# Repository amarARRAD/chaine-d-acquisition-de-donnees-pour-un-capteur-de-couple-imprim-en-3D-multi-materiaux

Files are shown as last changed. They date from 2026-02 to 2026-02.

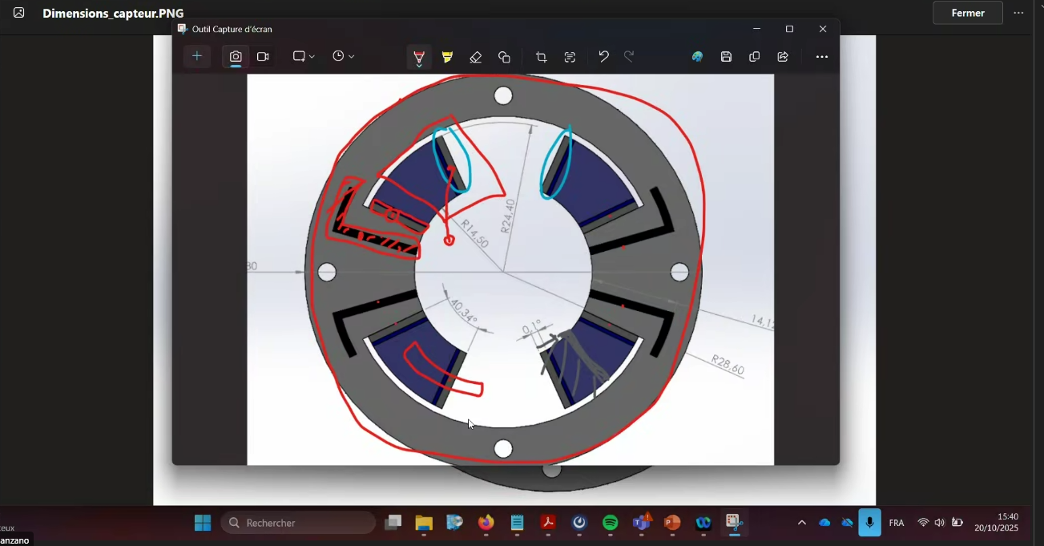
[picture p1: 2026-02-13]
Biblio/Biblio/Capture d'écran 2025-10-20 154038.png

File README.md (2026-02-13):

# Chaîne d’acquisition pour capteur de couple capacitif imprimé en 3D (ESP32-S3 + FDC1004)

Ce dépôt regroupe le travail réalisé dans le cadre du Master 2 EEEA (Systèmes embarqués) en collaboration avec l’Inria.  
Le projet vise à rendre autonome la mesure de couple d’un capteur capacitif imprimé en 3D multi-matériaux, destiné à une intégration dans un exosquelette.

## Principe
Le capteur comporte 4 structures capacitives. Lorsqu’un couple est appliqué, la déformation mécanique provoque des variations de capacité. Ces 4 mesures sont combinées pour obtenir une grandeur différentielle, puis un angle et enfin un couple estimé.

## Architecture matérielle
- **FDC1004** : convertisseur capacité-numérique (4 canaux) avec **blindage actif** (/Blinddd) pour limiter les capacités parasites.
- **ESP32-S3-WROOM-1** : récupération des mesures via **I2C**, traitement embarqué et communication.
- **PCB circulaire 2 couches** conçu pour être monté directement sur le capteur (plan de masse + plan de blindage).
- Interfaces prévues : **UART** (programmation / debug) et **CAN** (prévu pour intégration future exosquelette).

## Logiciel embarqué
Le traitement initialement réalisé sous MATLAB a été traduit en **C++ (ESP-IDF)** sous forme de librairie :
- driver I2C FDC1004 (lecture des 4 capacités, conversion en pF)
- calcul de la capacité différentielle (`Ctot`)
- estimation d’angle et de couple (modèle statique avec hystérésis + terme dynamique)

## Contenu du dépôt
- Fichiers **KiCad** (schéma + routage + fabrication)
- Code **C++ / ESP-IDF** (librairie capteur + exemples)
- Rapport (LaTeX) et annexes (datasheets / documents)

## Perspectives
- réintégration d’une **Flash externe**
- ajout de **filtrage numérique**
- ajout de capteurs complémentaires (température, IMU) pour améliorer la robustesse en conditions réelles

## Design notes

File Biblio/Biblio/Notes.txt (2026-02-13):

[1] Contexte du capteur : exosquelette développé à Rennes
[2] Caractérisation de la version actuelle du capteur de couple
[3] Capteur de couple similaire
[4] Algorithme de suivi d'hystérésis
[5] Mesure de capacités avec blindage (voir notamment section 6.2)

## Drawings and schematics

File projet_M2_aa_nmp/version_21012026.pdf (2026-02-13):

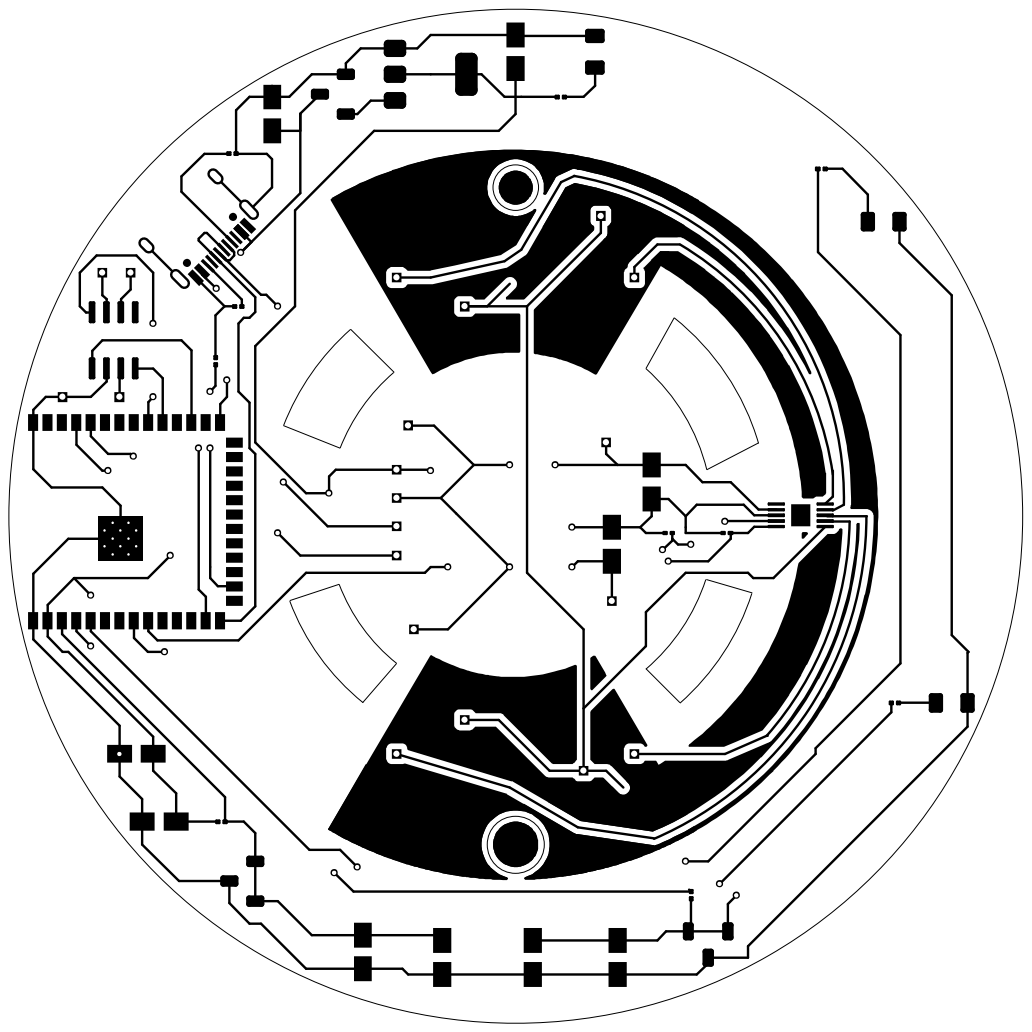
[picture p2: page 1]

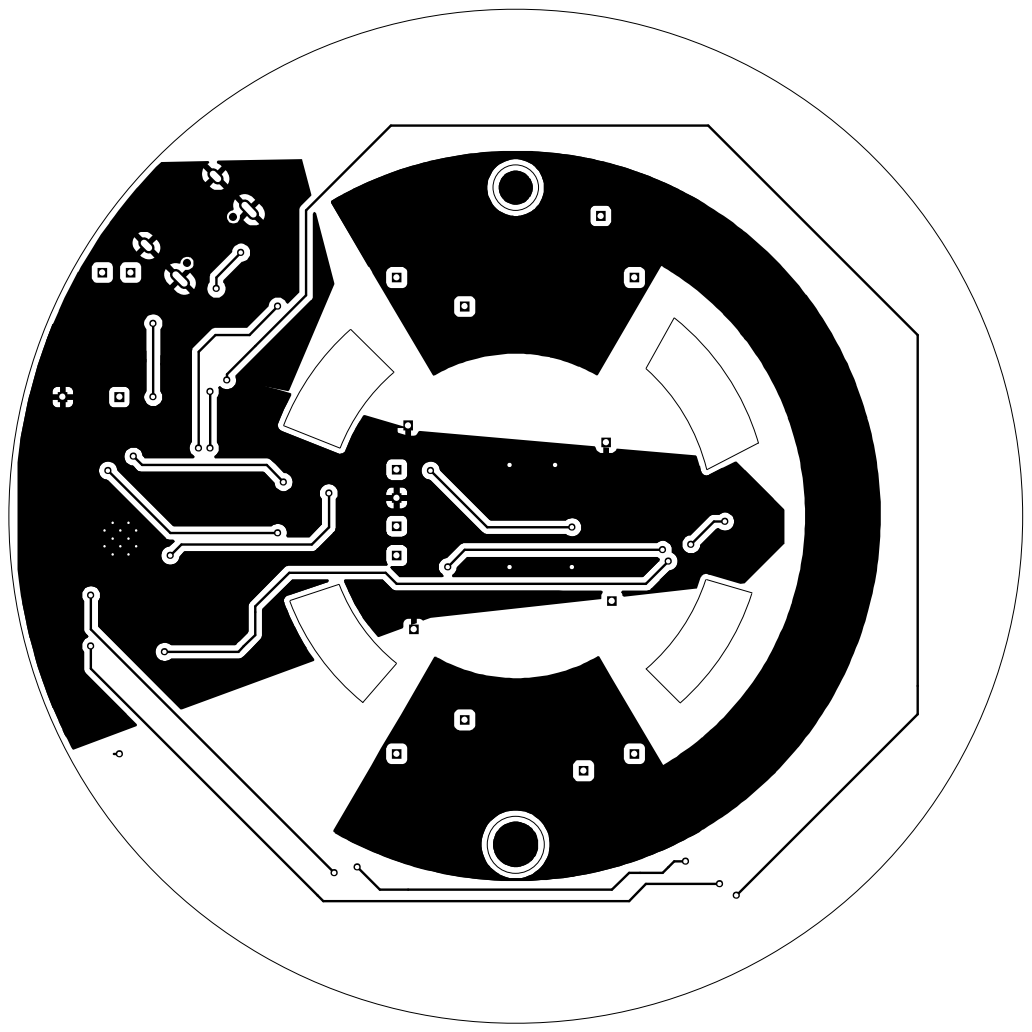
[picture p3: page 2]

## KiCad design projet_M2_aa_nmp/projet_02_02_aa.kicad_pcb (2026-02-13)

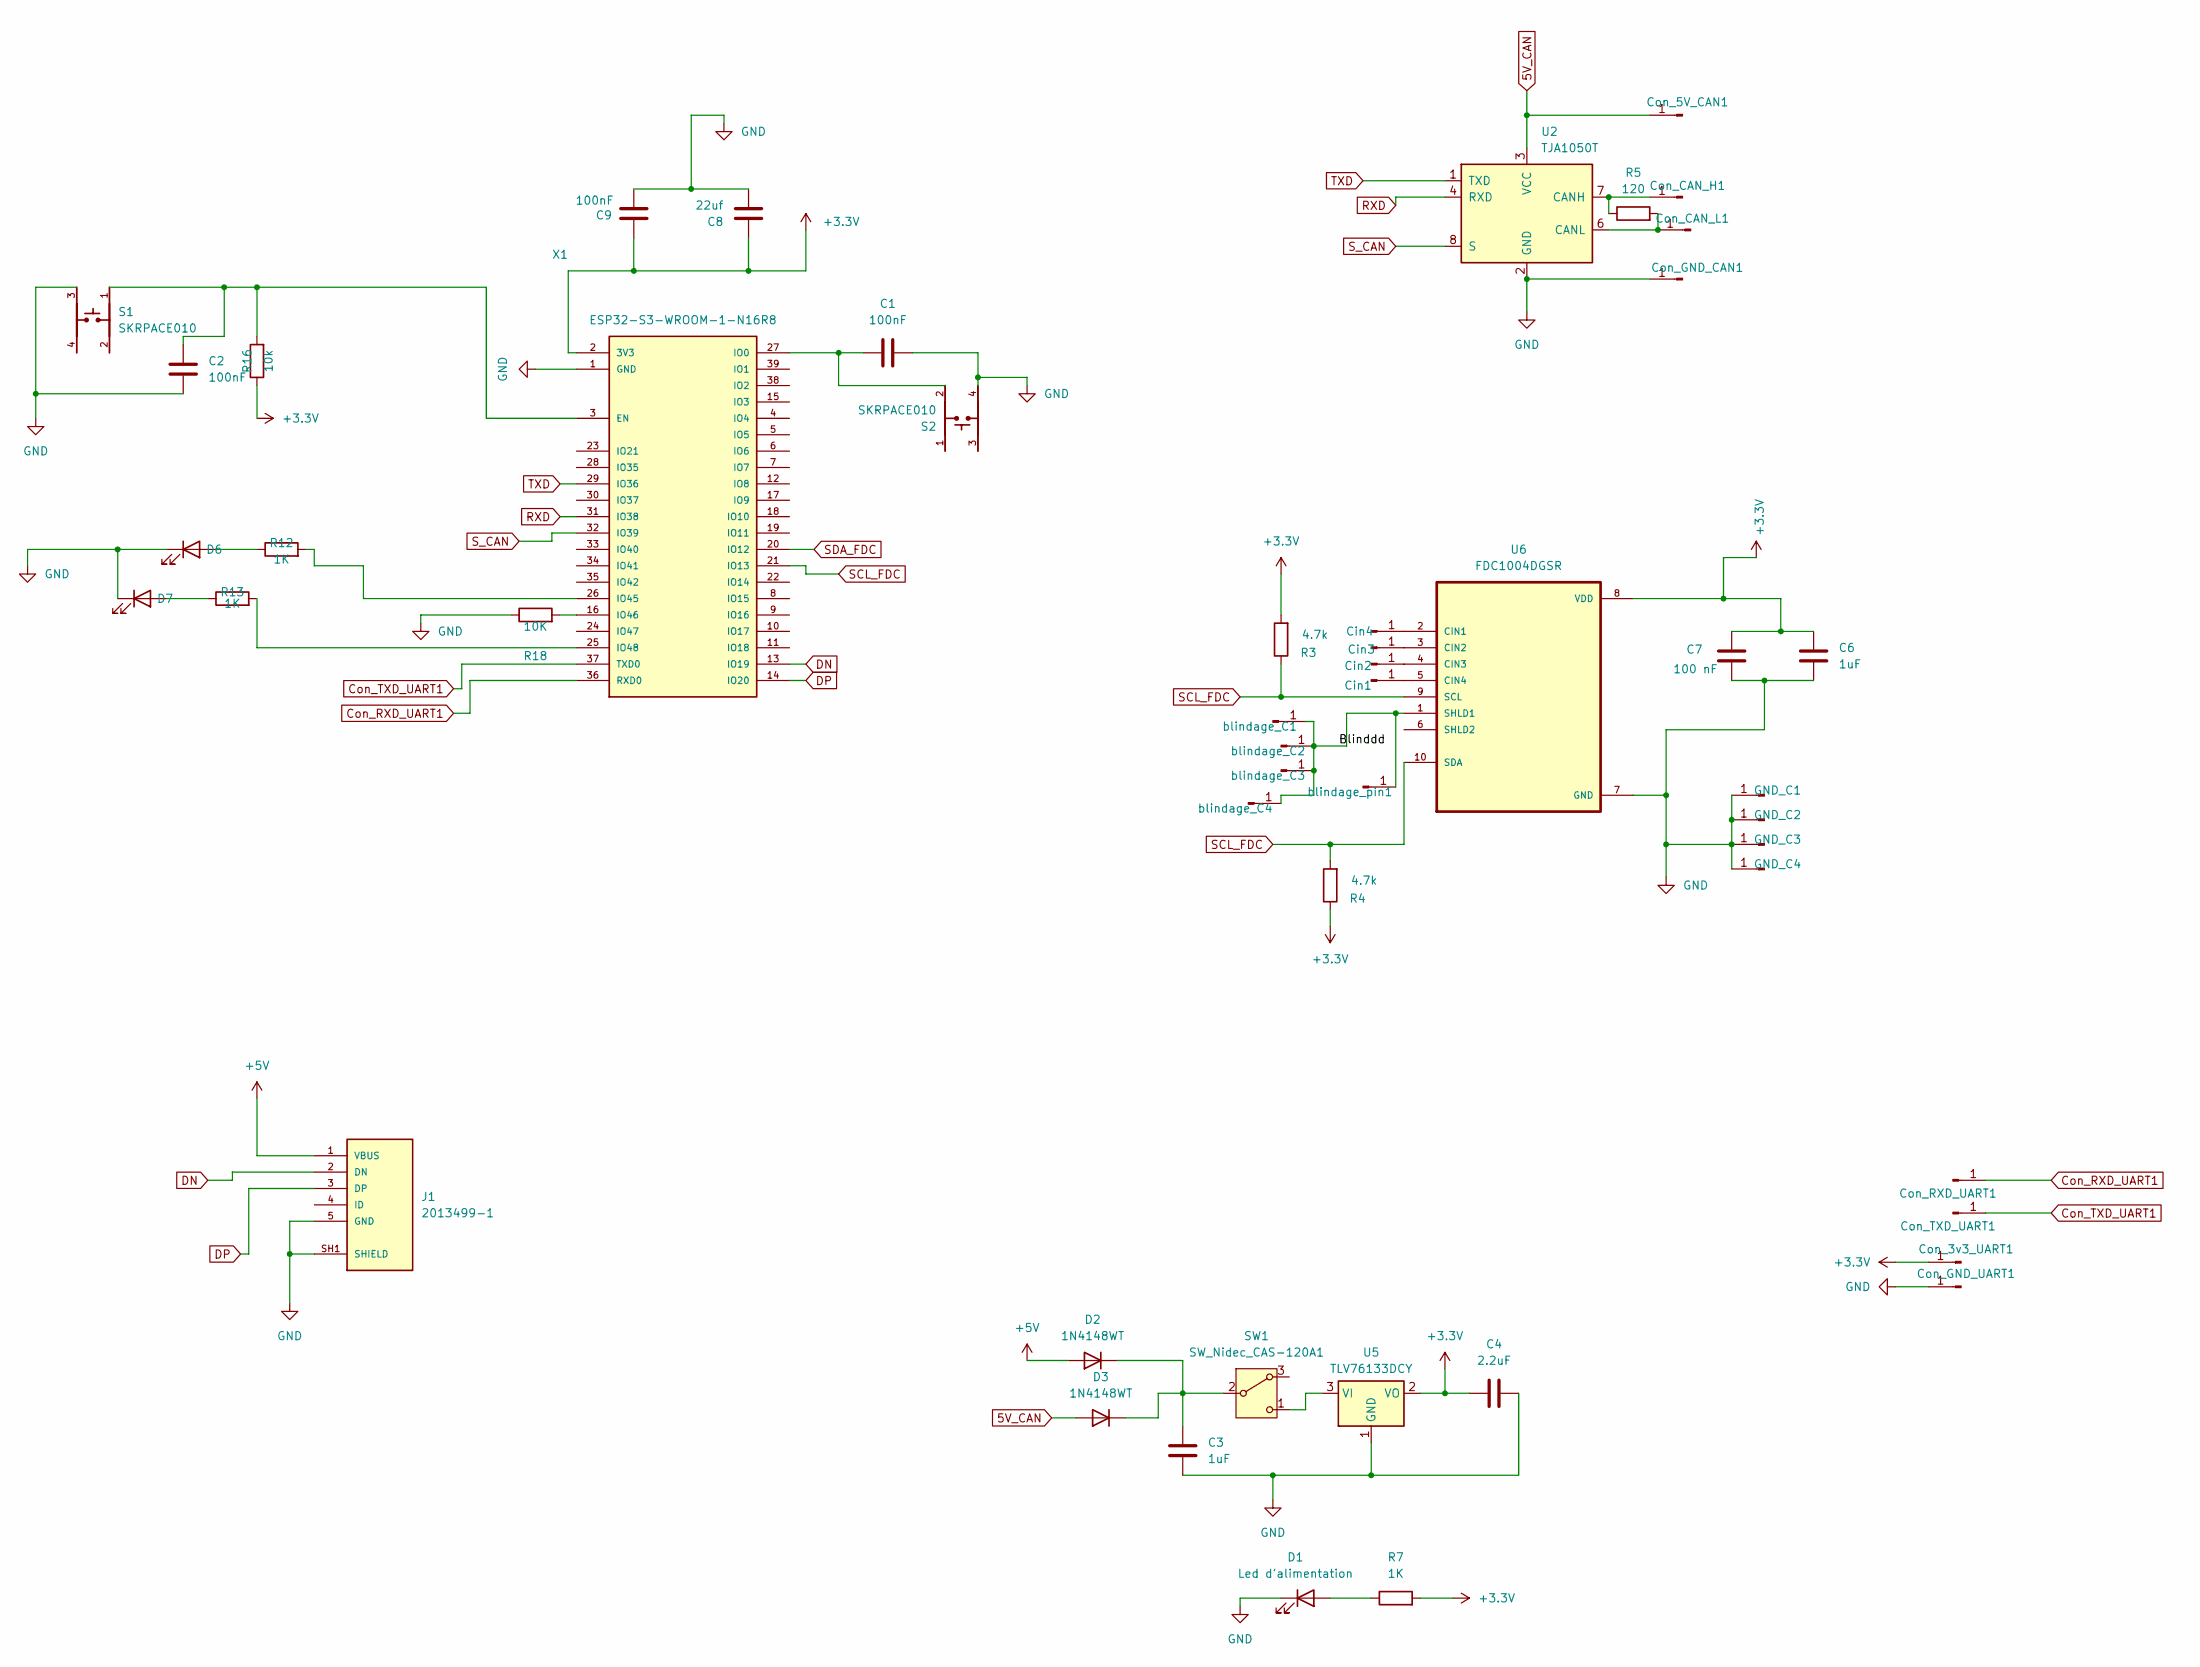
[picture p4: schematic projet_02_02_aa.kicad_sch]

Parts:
C1, C2, C9: 100nF; CP_Elec_3x5.3
C3, C6: 1uF; CP_Elec_3x5.3
C4: 2.2uF; CP_Elec_3x5.3
C7: 100 nF; CP_Elec_3x5.3
C8: 22uf; CP_Elec_3x5.3
Cin1, Cin2, Cin3, Cin4: Conn_01x01_Pin; PinHeader_1x01_P1.00mm_Vertical
Con_3v3_UART1, Con_5V_CAN1: Conn_01x01_Pin; PinHeader_1x01_P1.00mm_Vertical
Con_CAN_H1: Conn_01x01_Pin; PinHeader_1x01_P1.00mm_Vertical
Con_CAN_L1: Conn_01x01_Pin; PinHeader_1x01_P1.00mm_Vertical
Con_GND_CAN1: Conn_01x01_Pin; PinHeader_1x01_P1.00mm_Vertical
Con_GND_UART1: Conn_01x01_Pin; PinHeader_1x01_P1.00mm_Vertical
Con_RXD_UART1: Conn_01x01_Pin; PinHeader_1x01_P1.00mm_Vertical
Con_TXD_UART1: Conn_01x01_Pin; PinHeader_1x01_P1.00mm_Vertical
D1: Led d'alimentation; LED_1206_3216Metric
D2, D3: 1N4148WT; D_SOD-523
D6, D7: IR26-21C_L110_TR8; LED_1206_3216Metric
GND_C1, GND_C2, GND_C3, GND_C4: Conn_01x01_Pin; PinHeader_1x01_P1.00mm_Vertical
J1: 2013499-1; TE_2013499-1; PARTREV B5
R3, R4: 4.7k; R_0201_0603Metric
R5: 120; R_0201_0603Metric
R7, R12, R13: 1K; R_0201_0603Metric
R16: 10k; R_0201_0603Metric
R18: 10K; R_0201_0603Metric
S1, S2: SKRPACE010; SW_SKRPACE010
SW1: SW_Nidec_CAS-120A1; Nidec_Copal_CAS-120A
U2: TJA1050T; SOIC-8_3.9x4.9mm_P1.27mm
U5: TLV76133DCY; SOT-223-3_TabPin2
U6: FDC1004DGSR; MSOP-10-1EP_3x3mm_P0.5mm_EP1.73x1.98mm
X1: ESP32-S3-WROOM-1-N16R8; ESP32S3WROOM1N8R2; MANUFACTURER_PART_NUMBER ESP32-S3-WROOM-1-N16R8
blindage_C1, blindage_C2, blindage_C3, blindage_C4: Conn_01x01_Pin; PinHeader_1x01_P1.00mm_Vertical
blindage_pin1: Conn_01x01_Pin; PinHeader_1x01_P1.00mm_Vertical

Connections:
5V_CAN: Con_5V_CAN1.1, D3.2 (A), U2.3 (VCC)
+3.3V: C4.1, C6.2, C7.2, C8.2, C9.2, Con_3v3_UART1.1, R3.2, R4.1, R7.2, R16.1, U5.2 (VO), U6.8 (VDD), X1.2 (3V3)
+5V: D2.2 (A), J1.1 (VBUS)
/Blinddd: U6.1 (SHLD1), blindage_C1.1, blindage_C2.1, blindage_C3.1, blindage_C4.1, blindage_pin1.1
Con_RXD_UART1: Con_RXD_UART1.1, X1.36 (RXD0)
Con_TXD_UART1: Con_TXD_UART1.1, X1.37 (TXD0)
DN: J1.2 (DN), X1.13 (IO19)
DP: J1.3 (DP), X1.14 (IO20)
GND: C1.2, C2.1, C3.2, C4.2, C6.1, C7.1, C8.1, C9.1, Con_GND_CAN1.1, Con_GND_UART1.1, D1.1 (K), D6.1 (K), D7.1 (K), GND_C1.1, GND_C2.1, GND_C3.1, GND_C4.1, J1.5 (GND), J1.SH1 (SHIELD), J1.SH2 (SHIELD), J1.SH3 (SHIELD), J1.SH4 (SHIELD), J1.SH5 (SHIELD), J1.SH6 (SHIELD), R18.1, S1.3, S2.4, U2.2 (GND), U5.1 (GND), U6.7 (GND), X1.1 (GND), X1.40 (GND), X1.41 (GND), X1.42 (GND), X1.43 (GND), X1.44 (GND), X1.45 (GND), X1.46 (GND), X1.47 (GND), X1.48 (GND), X1.49 (GND)
unnamed: Cin1.1, U6.5 (CIN4)
unnamed: Cin2.1, U6.4 (CIN3)
unnamed: Cin3.1, U6.3 (CIN2)
unnamed: Cin4.1, U6.2 (CIN1)
unnamed: Con_CAN_H1.1, R5.1, U2.7 (CANH)
unnamed: Con_CAN_L1.1, R5.2, U2.6 (CANL)
unnamed: D1.2 (A), R7.1
unnamed: C3.1, D2.1 (K), D3.1 (K), SW1.2 (B)
unnamed: D6.2 (A), R12.1
unnamed: D7.2 (A), R13.1
unnamed: SW1.1 (C), U5.3 (VI)
unnamed: C2.2, R16.2, S1.1, X1.3 (EN)
unnamed: C1.1, S2.2, X1.27 (IO0)
unnamed: R12.2, X1.26 (IO45)
unnamed: R18.2, X1.16 (IO46)
unnamed: R13.2, X1.25 (IO48)
RXD: U2.4 (RXD), X1.31 (IO38)
S_CAN: U2.8 (S), X1.32 (IO39)
TXD: U2.1 (TXD), X1.29 (IO36)

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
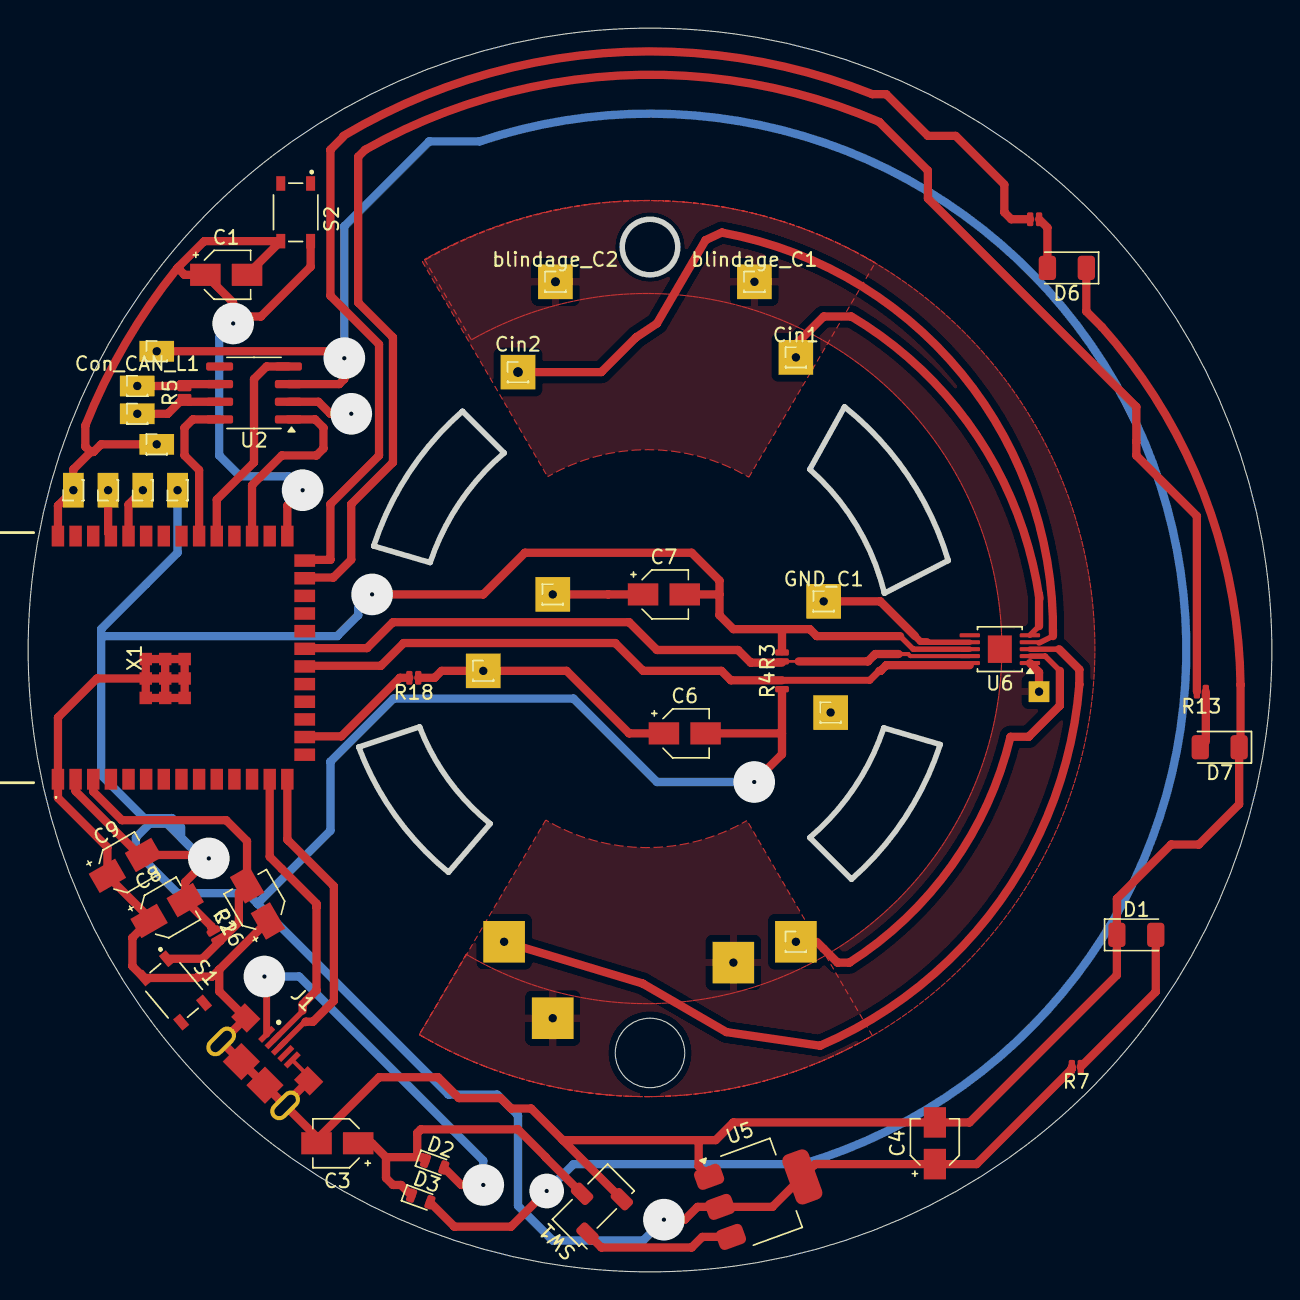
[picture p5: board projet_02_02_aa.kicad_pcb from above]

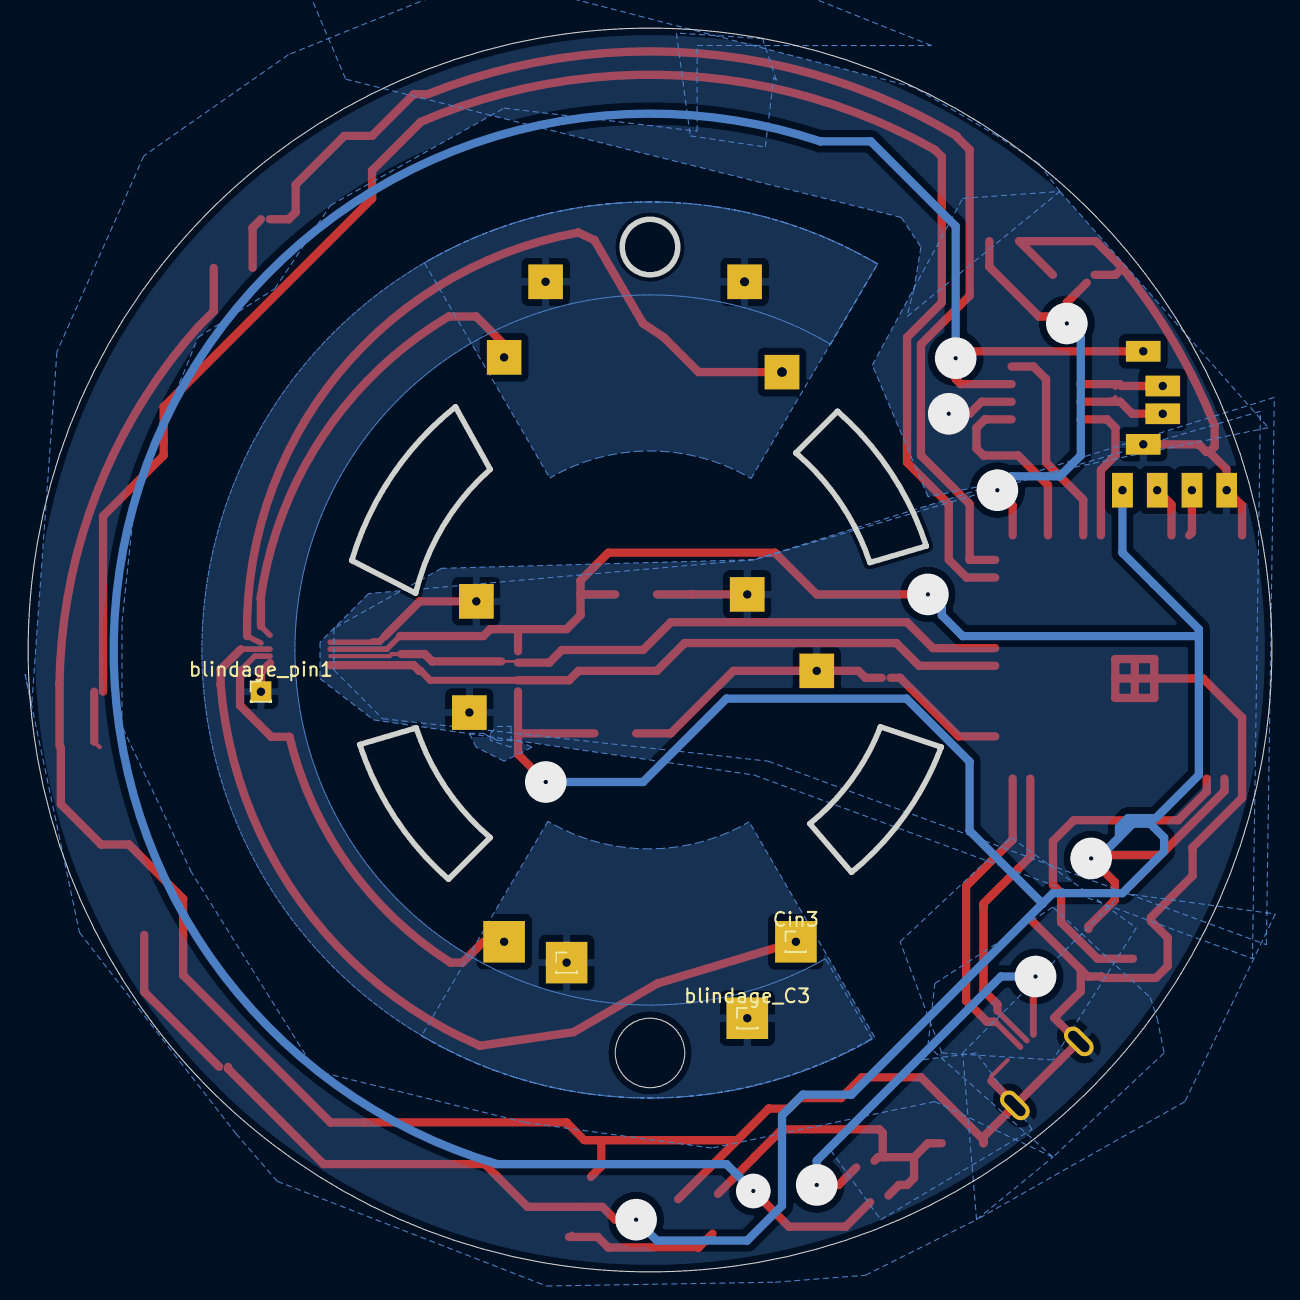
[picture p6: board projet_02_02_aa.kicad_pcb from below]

Board: 2 copper layers, 89.5 x 89.5 mm, 50 parts (4 on the bottom side), 30 nets.
